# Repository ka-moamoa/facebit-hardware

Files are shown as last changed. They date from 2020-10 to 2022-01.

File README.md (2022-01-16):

# Smart PPE Hardware

The FaceBit circuit board contains all of the power harvesting, sense, and compute functionality demonstrated in the paper, plus a few extra capabilities we didn't use. This repository contains the Altium project with a [tagged release](https://github.com/ka-moamoa/facebit-hardware/releases/tag/paper-release) of the version manufactured for the paper. Note that Altium offers a [free student license](https://www.altium.com/solutions/academic-programs/student-licenses). 

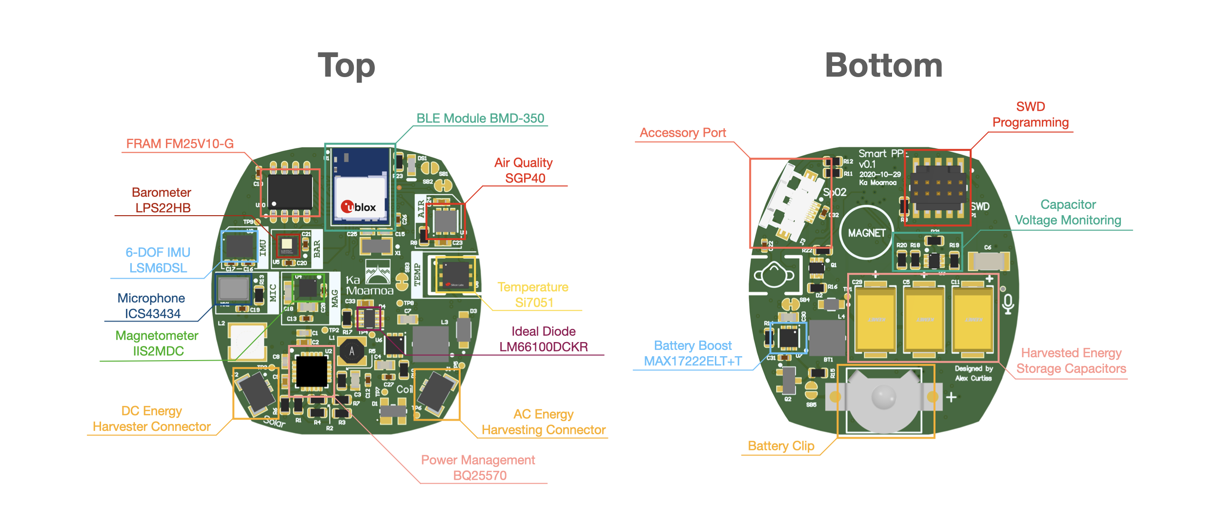
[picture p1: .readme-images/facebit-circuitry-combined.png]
Labeled Circuit Board


## Overview

FaceBit is small enough to fit comfortably in either an N95 or surgical mask (1.2" wide x 1.3" tall). It is clipped in place by 1) gluing a magnet to the underside of the board in the space provided, 2) positioning the board in the mask with the magnet facing toward the mask and 3) attaching a magnet to the other side. 

The board features an NRF2832 SoC from Nordic Semiconductor, which is packaged with a chip antenna on the pre-certified BMD-350 BLE Module. With a goal of using this platform to explore a wide range of health and environmental sensing applications, this version includes six sensors, which can be seen in the images. Only three are used in the paper: the LPS22HB barometer, the LSM6DSL 6-DOF Inertial Measurement Unit (IMU), and the Si7051 temperature sensor. In future versions, we expect to reduce the number of sensors and (therefore) reduce the size and cost of the board.

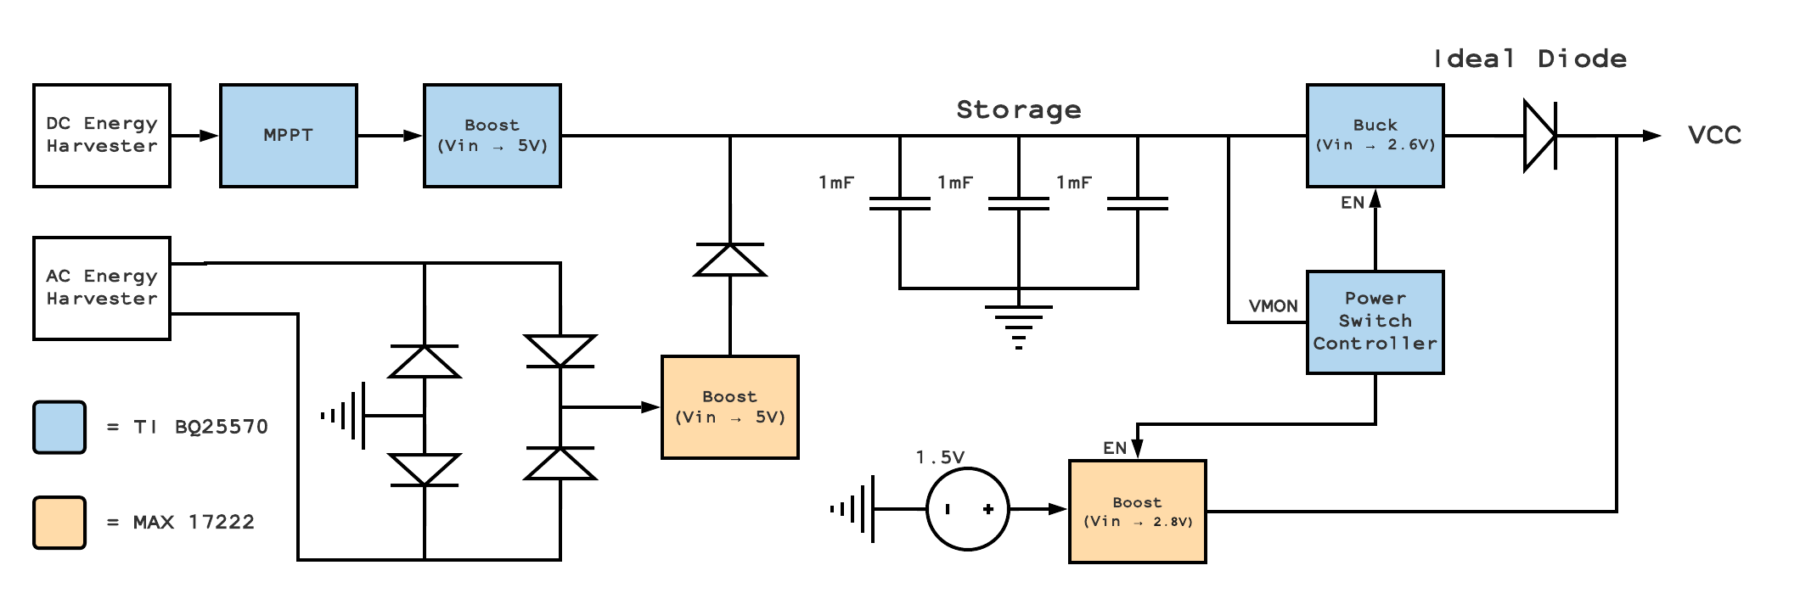
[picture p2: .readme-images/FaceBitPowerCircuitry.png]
Power Architecture
We adopt a flexible hybrid approach with regards to power:  We include a battery holder for a small, 105 mWh primary cell, but also include the circuitry and storage to power the board using energy harvested from both DC (e.g. solar) or AC (e.g. shaker) sources. Three tantalum capacitors on the bottom of the board combine to provide 3 mF of storage capacity for harvested energy. These are charged by Texas Instruments' BQ25570 power management IC, which incorporates a boost converter with MPPT, intelligent charging circuitry, and a buck converter to reduce the voltage from the storage elements to a level tolerated by the system. The tantalum capacitors are charged to 5V (80\% of their 6.3V rating), and so are able to store a total of 10.4 \(\mu\)Wh. We use the "power good" indicator on the BQ25570 IC to implement an intelligent switch that automatically decides which source to draw power from based on the voltage of the capacitors. By default, the system draws its power from the battery (when one is present). When the storage capacitor voltage exceeds a resistor-programmed threshold (3.0V in our application), the BQ25570 begins to draw from them and the battery boost converter is disabled, which protects the battery from reverse current.  When the storage capacitors fall below 2.6V, the BQ25570 switches off it's buck converter and system power is once again drawn from the battery. An ideal diode (LM66100DCKR) prevents reverse flow into the energy harvesting circuitry while the battery boost converter is active.

This power architecture allows for a relatively long battery life (the energy density of primary cells being greater than that of rechargeable cells), while still maintaining the ability to store and use harvested energy. The device can also operate in a mode where it uses only harvested energy, activated simply by not placing a battery in the connector. This flexible architecture suited the development process, but it is also possible to further simplify and miniaturize the board by using either only a rechargeable cell or only energy storage capacitors. 

### Errata

The tagged release includes fixes for the minor issues that required board rework after we received the boards (e.g. wrong resistor value). Still, some of the design choices, particularly those around the power architecture, limit the lowest possible sleep current of the board to around 30 uA. Version 2.0 is in the works which includes a revamped power architecture to address those issues.

The battery holder on this board is barely worth your time. It is ever so slightly too small for all of the batteries we were able to find, which means that over time it inevitably pops off the board, requiring a careful resoldering to the correct height. It's helpful to put a very thin layer of solder on the ground pad to facilitate contact with the battery.

Finally, as noted on the schematics the selected microphone unfortunately does not work with the NRF52. As you can see in [this issue](https://devzone.nordicsemi.com/f/nordic-q-a/24589/configuring-i2s-for-ics43434), the I2S frame width is incompatible with the nordic peripheral.

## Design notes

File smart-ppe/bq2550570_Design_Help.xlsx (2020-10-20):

User Input | VBIAS | 1.21 | V
Fixed
 | Comparator threshold for VSTOR of charger. |  |  |  |  | Comparator threshold voltages indicating when |  |  |  |  | For the bq25570 only, comparator threshold |  |  |  |  | Maximum power point threshold, e.g. ~0.7-0.8 of
 | Typically the max storage element voltage, |  |  |  |  | VSTOR has risen above VBAT_OK_HYST or fallen |  |  |  |  | for VOUT of buck converter. |  |  |  |  | solar panel's open circuit voltage.
 | e.g. 4.2V for LiIon battery. |  |  |  |  | below VBAT_OK.
 | VBAT_UV < VBAT_OV < 5.5V |  |  |  |  | VBAT_OV > VBAT_OK_HYST > VBAT_UV |  |  |  |  | 1.3V < VOUT < VBAT_OV |  |  |  |  | MPPT
Desired |  |  |  |  |  | RSUM1 | 13 | MW |  |  |  |  |  |  |  | RSUM1 | 20 | MW
Desired | RSUM1 | 13 | MW |  |  | VBAT_OK | 2.8 | V | > VBAT_UV |  | RSUM1 | 13 | MW |  |  | VIN_DC(OC) | 1 | V | Open Circuit Volts
Desired | VBAT_OV | 4 | V |  |  | VBAT_OK_HYST | 3.1 | V | > VBAT_OK |  | VOUT | 2.15 | V |  |  | VREF_SAMP | 0.9 | V | MPP voltage
 |  |  |  |  |  |  |  | closest 1% resistor1 |  |  |  |  |  |  |  |  |  | closest 1% resistor1
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

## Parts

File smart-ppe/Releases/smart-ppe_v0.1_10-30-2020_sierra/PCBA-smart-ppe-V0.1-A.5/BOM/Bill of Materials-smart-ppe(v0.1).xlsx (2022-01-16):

Line # | Name | Designator | Description | Manufacturer 1 | Manufacturer Part Number 1 | Manufacturer Lifecycle 1 | Supplier 1 | Supplier Part Number 1
 | 2988 | BT1 | BATTERY RETAINER COIN 7.9MM SMD | Keystone Electronics | 2988 | Volume Production | Newark | 25T0413
 | GRM155R60J475ME47D | C1 |  | Murata | GRM155R60J475ME47D | Volume Production | Digi-Key | 490-5915-6-ND
 | GRM155R71H103KA88D | C2 | Chip Capacitor, 10 nF, +/- 10%, 50 V, -55 to 125 degC, 0402 (1005 Metric), RoHS, Tape and Reel | Murata | GRM155R71H103KA88D | Volume Production | Arrow Electronics | GRM155R71H103KA88D
 | C1608X5R0J226M080AC | C3 | Chip Capacitor, 22 uF, +/- 20%, 6.3 V, -55 to 85 degC, 1608 (0603 Metric), RoHS, Tape and Reel | TDK | C1608X5R0J226M080AC | Volume Production | Newark | 65T7792
 | GRM188R60J106ME47D | C4 |  | Murata | GRM188R60J106ME47D | Volume Production | Arrow Electronics | GRM188R60J106ME47D
 | T495X108K006ATE100 | C5 | CAP TANT 1000UF 10% 6.3V 2917 | KEMET | T495X108K006ATE100 | Volume Production | Arrow Electronics | T495X108K006ATE100
 | C3216X5R1A107M160AC | C6 | Chip Capacitor, 100 uF, +/- 20%, 10 V, -55 to 85 degC, 1206 (3216 Metric), RoHS, Tape and Reel | TDK | C3216X5R1A107M160AC | Volume Production | Newark | 12T1945
 | GRM188R60J106ME47D | C7 |  | Murata | GRM188R60J106ME47D | Volume Production | Arrow Electronics | GRM188R60J106ME47D
 | GRM155R60J475ME47D | C8 |  | Murata | GRM155R60J475ME47D | Volume Production | Digi-Key | 490-5915-6-ND
 | GRM155R71H103KA88D | C9 | Chip Capacitor, 10 nF, +/- 10%, 50 V, -55 to 125 degC, 0402 (1005 Metric), RoHS, Tape and Reel | Murata | GRM155R71H103KA88D | Volume Production | Arrow Electronics | GRM155R71H103KA88D
 | Capacitor 100nF +/-20% 25V 0402 | C10 | Chip Capacitor, 100nF +/-20%, 25V, 0402, Thickness 0.6 mm | Samsung | CL05A104KA5NNNC | Volume Production | Newark | 82AC9174
 | T495X108K006ATE100 | C11 | CAP TANT 1000UF 10% 6.3V 2917 | KEMET | T495X108K006ATE100 | Volume Production | Arrow Electronics | T495X108K006ATE100
 | Capacitor 100nF +/-20% 25V 0402 | C12 | Chip Capacitor, 100nF +/-20%, 25V, 0402, Thickness 0.6 mm | Samsung | CL05A104KA5NNNC | Volume Production | Newark | 82AC9174
 | Capacitor 100nF +/-20% 25V 0402 | C13 | Chip Capacitor, 100nF +/-20%, 25V, 0402, Thickness 0.6 mm | Samsung | CL05A104KA5NNNC | Volume Production | Newark | 82AC9174
 | Capacitor 100nF +/-20% 25V 0402 | C14 | Chip Capacitor, 100nF +/-20%, 25V, 0402, Thickness 0.6 mm | Samsung | CL05A104KA5NNNC | Volume Production | Newark | 82AC9174
 | 04025A8R2JAT2A | C15 |  | Kyocera AVX | 04025A8R2JAT2A | Volume Production | Arrow Electronics | 04025A8R2JAT2A
 | Capacitor 100nF +/-20% 25V 0402 | C16 | Chip Capacitor, 100nF +/-20%, 25V, 0402, Thickness 0.6 mm | Samsung | CL05A104KA5NNNC | Volume Production | Newark | 82AC9174
 | Capacitor 100nF +/-20% 25V 0402 | C17 | Chip Capacitor, 100nF +/-20%, 25V, 0402, Thickness 0.6 mm | Samsung | CL05A104KA5NNNC | Volume Production | Newark | 82AC9174
 | CAP 220nF 25V 0603(1608) | C18 | CAP 220nF 25V ±10% 0603 (1608 Metric) Thickness 1mm SMD | Kyocera AVX | 06033C224KAT2A | Volume Production | Newark | 85R5672
 | Capacitor 100nF +/-20% 25V 0402 | C19 | Chip Capacitor, 100nF +/-20%, 25V, 0402, Thickness 0.6 mm | Samsung | CL05A104KA5NNNC | Volume Production | Newark | 82AC9174
 | Capacitor 100nF +/-20% 25V 0402 | C20 | Chip Capacitor, 100nF +/-20%, 25V, 0402, Thickness 0.6 mm | Samsung | CL05A104KA5NNNC | Volume Production | Newark | 82AC9174
 | Capacitor 100nF +/-20% 25V 0402 | C21 | Chip Capacitor, 100nF +/-20%, 25V, 0402, Thickness 0.6 mm | Samsung | CL05A104KA5NNNC | Volume Production | Newark | 82AC9174
 | Capacitor 100nF +/-20% 25V 0402 | C22 | Chip Capacitor, 100nF +/-20%, 25V, 0402, Thickness 0.6 mm | Samsung | CL05A104KA5NNNC | Volume Production | Newark | 82AC9174
 | CC0402KRX5R5BB105 | C23 | Chip Capacitor, 1 uF, +/- 10%, 6.3 V, -55 to 85 degC, 1005 (0402 Metric), RoHS, Tape and Reel | Yageo | CC0402KRX5R5BB105 | Volume Production | Newark | 65R7644
 | CC0402KRX5R5BB105 | C24 | Chip Capacitor, 1 uF, +/- 10%, 6.3 V, -55 to 85 degC, 1005 (0402 Metric), RoHS, Tape and Reel | Yageo | CC0402KRX5R5BB105 | Volume Production | Newark | 65R7644
 | 04025A8R2JAT2A | C25 |  | Kyocera AVX | 04025A8R2JAT2A | Volume Production | Arrow Electronics | 04025A8R2JAT2A
 | Capacitor 100nF +/-20% 25V 0402 | C26 | Chip Capacitor, 100nF +/-20%, 25V, 0402, Thickness 0.6 mm | Samsung | CL05A104KA5NNNC | Volume Production | Newark | 82AC9174
 | Capacitor 100nF +/-20% 25V 0402 | C27 | Chip Capacitor, 100nF +/-20%, 25V, 0402, Thickness 0.6 mm | Samsung | CL05A104KA5NNNC | Volume Production | Newark | 82AC9174
 | GRM188R60J106ME47D | C28 |  | Murata | GRM188R60J106ME47D | Volume Production | Arrow Electronics | GRM188R60J106ME47D
 | T495X108K006ATE100 | C29 | CAP TANT 1000UF 10% 6.3V 2917 | KEMET | T495X108K006ATE100 | Volume Production | Arrow Electronics | T495X108K006ATE100
 | GRM188R60J106ME47D | C30 |  | Murata | GRM188R60J106ME47D | Volume Production | Arrow Electronics | GRM188R60J106ME47D
 | Capacitor 100nF +/-20% 25V 0402 | C31 | Chip Capacitor, 100nF +/-20%, 25V, 0402, Thickness 0.6 mm | Samsung | CL05A104KA5NNNC | Volume Production | Newark | 82AC9174
 | Capacitor 100nF +/-20% 25V 0402 | C32 | Chip Capacitor, 100nF +/-20%, 25V, 0402, Thickness 0.6 mm | Samsung | CL05A104KA5NNNC | Volume Production | Newark | 82AC9174
 | CC0402KRX5R5BB105 | C33 | Chip Capacitor, 1 uF, +/- 10%, 6.3 V, -55 to 85 degC, 1005 (0402 Metric), RoHS, Tape and Reel | Yageo | CC0402KRX5R5BB105 | Volume Production | Newark | 65R7644
 | BAS3007A-RPP | D1 | Low VF Schottky Diode Array, 30 V VR, 900 mA IF, SOT143, Reel, Green | Infineon | BAS3007A-RPP | Volume Production | Arrow Electronics | BAS3007ARPPE6327HTSA1
 | BAT54HT1G | D2 | Schottky Barrier Diode, 2-Pin SOD-323, Pb-Free, Tape and Reel | ON Semiconductor / Fairchild | BAT54HT1G | Volume Production | Future Electronics | 7645070
 | BZT52C5V1-7-F | D3 | Surface Mount Zener Diode, 5.1 V, -65 to 150 degC, 2-Pin SMD (SOD-123), RoHS, Tape and Reel | Diodes | BZT52C5V1-7-F | Volume Production | Newark | 81AC7614
 | LM66100DCKR | D4 | Diode | Texas Instruments | LM66100DCKR | Unknown | Digi-Key | 296-53541-1-ND
 | HSMG-C190 | DS1 | Chip LED, Green, 2.2 V, -40 to 85 degC, 2-Pin SMD, RoHS, Tape and Reel | Broadcom Avago | HSMG-C190 | Volume Production | Mouser | 630-HSMG-C190
 | SM02B-SURS-TF_LF__SN | J1 | Connector | JST (JAPAN SOLDERLESS TERMINALS) | SM02B-SURS-TF(LF)(SN)
 | SM02B-SURS-TF(LF)(SN) | J2 | Connector | JST (JAPAN SOLDERLESS TERMINALS) | SM02B-SURS-TF(LF)(SN)
 | 54550-0571 | J3 | 0.5 mm Pitch Easy-On(TM) Type FPC Connector, 1.2 mm Mated Height, Right Angle, ZIF, SMT, Top Contact, 5 Circuits, -20 to 85 degC, ELV and RoHS Compliant, Tape and Reel | Molex | 54550-0571 | Volume Production | Digi-Key | WM8824DKR-ND
 | 744029100 | L1 | SMD Shielded Tiny Power Inductor WE-TPC, L = 10.0 µH | Wurth Electronics | 744029100 | Volume Production | Digi-Key | 732-1091-1-ND
 | 744031220 | L2 | SMD Shielded Tiny Power Inductor WE-TPC, L = 22.0 µH | Wurth Electronics | 744031220 | Volume Production | Digi-Key | 732-1012-6-ND
 | 74438357022 | L3 | WURTH ELEKTRONIK - 74438357022 - INDUCTOR, 2.2UH, 5.2A, 20%, SHIELDED | Wurth Electronics | 74438357022 | Unknown | Digi-Key | 732-11201-6-ND
 | 74438357022 | L4 | WURTH ELEKTRONIK - 74438357022 - INDUCTOR, 2.2UH, 5.2A, 20%, SHIELDED | Wurth Electronics | 74438357022 | Unknown | Digi-Key | 732-11201-6-ND
 | Mic_InvenSense_ICS-43434_eec | MK1 | MIC MEMS MULTI-MODE OMNI -26DB | TDK InvenSense | ICS-43434 | New Product | Digi-Key | 1428-1066-6-ND
 | FTSH-105-01-F-DV-K-P-TR | P1 | CONN HEADER SMD 10POS 1.27MM | Samtec | FTSH-105-01-F-DV-K-P-TR | Volume Production | Newark | 25AC9619
 | DMC2400UV-7 | Q1 | Complementary Pair Enhancement Mode MOSFET, 20 V N-Channel, -20 V P-Channel, -55 to 150 degC, 6-Pin SOTFL (SOT563), RoHS, Tape and Reel | Diodes | DMC2400UV-7 | Volume Production | Newark | 79AH1251
 | SI2323DS-T1-E3 | Q2 | P-Channel MOSFET, 20 V, -55 to 150 degC, 3-Pin TO-236, RoHS, Tape and Reel | Vishay | SI2323DS-T1-E3 | Volume Production | Newark | 06J7584
 | DMC2400UV-7 | Q3 | Complementary Pair Enhancement Mode MOSFET, 20 V N-Channel, -20 V P-Channel, -55 to 150 degC, 6-Pin SOTFL (SOT563), RoHS, Tape and Reel | Diodes | DMC2400UV-7 | Volume Production | Newark | 79AH1251
 | RES_0603 | R1 | Resistor Ω % 0603 | Vishay | CRCW06038M25FKEA |  | Digi-Key | 541-8.25MHCT-ND
 | RES_0603 | R2 | Resistor Ω % 0603 | Vishay | CRCW06033M01FKEA |  | Digi-Key | 541-3.01MHCT-ND
 | RES_0603 | R3 | Resistor Ω % 0603 | Vishay | CRCW06037M15FKEA |  | Digi-Key | 541-7.15MHCT-ND
 | RES_0603 | R4 | Resistor Ω % 0603 | Stackpole Electronics | RMCF0603FT4M64 |  | Digi-Key | RMCF0603FT4M64CT-ND
 | RES_0603 | R5 | Resistor Ω % 0603 | Vishay | CRCW06035M62FKEA |  | Digi-Key | 541-5.62MHCT-ND
 | RES_0603 | R6 | Resistor Ω % 0603 | Stackpole Electronics | RMCF0603FT4M64 |  | Digi-Key | RMCF0603FT4M64CT-ND
 | RES_0603 | R7 | Resistor Ω % 0603 | Vishay | CRCW06035M23FKEA |  | Digi-Key | 541-5.23MHCT-ND
 | RES_0603 | R8 | Resistor Ω % 0603 | Yageo | RC0603FR-074R7L |  | Digi-Key | YAG3371CT-ND
 | RES_0603 | R9 | Resistor Ω % 0603 | Panasonic | ERJ-3EKF4701V |  | Digi-Key | P4.70KHCT-ND
 | RES_0603 | R10 | Resistor Ω % 0603 | Stackpole Electronics | HMC0603JT33M0 |  | Digi-Key | HMC0603JT33M0CT-ND
 | RES_0603 | R11 | Resistor Ω % 0603 | Panasonic | ERJ-3EKF4701V |  | Digi-Key | P4.70KHCT-ND
 | RES_0603 | R12 | Resistor Ω % 0603 | Panasonic | ERJ-3EKF4701V |  | Digi-Key | P4.70KHCT-ND
 | RES_0603 | R13 | Resistor Ω % 0603 | Yageo | RC0603FR-07100KL |  | Digi-Key | 311-100KHRCT-ND
 | RES_0603 | R14 | Resistor Ω % 0603 | Vishay | CRCW0603536RFKEA |  | Digi-Key | 541-536HCT-ND
 | RES_0603 | R15 | Resistor Ω % 0603 | Samsung | RC1608F335CS |  | Arrow Electronics | RC1608F335CS
 | RES_0603 | R16 | Resistor Ω % 0603 | Vishay | CRCW06031M00FKEA |  | Digi-Key | 541-1.00MHCT-ND
 | RES_0603 | R17 | Resistor Ω % 0603 | Vishay | CRCW06031M00FKEA |  | Digi-Key | 541-1.00MHCT-ND
 | RES_0603 | R18 | Resistor Ω % 0603 | Vishay | CRCW0603180KFKEA |  | Digi-Key | 541-180KHCT-ND
 | RES_0603 | R19 | Resistor Ω % 0603 |  |  |  | Digi-Key | 541-1.00MHCT-ND
 | RES_0603 | R20 | Resistor Ω % 0603 | Yageo | RC0603FR-07100KL |  | Digi-Key | 311-100KHRCT-ND
 | RES_0603 | R21 | Resistor Ω % 0603 | Vishay | CRCW06031M00FKEA |  | Digi-Key | 541-1.00MHCT-ND
 | RES_0603 | R22 | Resistor Ω % 0603 | Vishay | CRCW06031M00FKEA |  | Digi-Key | 541-1.00MHCT-ND
 | RES_0603 | R23 | Resistor Ω % 0603 | Panasonic | ERJ3EKF4700V |  | Digi-Key | P470HCT-ND
 | BMD-350 | U1 | u-blox BMD-350 Bluetooth 5 module | u-blox | BMD-350-A-R | Unknown | Digi-Key | 672-BMD-350-A-RDKR-ND
 | BQ25570RGRR | U2 | Battery Management Low Pwr Harvester Pwr Mgmt IC | Texas Instruments | BQ25570RGRR | Volume Production | Arrow Electronics | BQ25570RGRR
 | LSM6DSLTR | U3 | iNEMO Inertial Module:Always-on 3D Accelerometer and 3D Gyroscope, 1.71 to 3.6 V, -40 to 85 degC, 14-Pin LGA, RoHS, Tape and Reel | STMicroelectronics | LSM6DSLTR | Not Recommended for New Design | Arrow Electronics | LSM6DSLTR
 | IIS2MDCTR | U4 | HIGH ACCURACY ULTRA-LOW-POWER 3- | STMicroelectronics | IIS2MDCTR | Unknown | Digi-Key | 497-17728-6-ND
 | LPS22HBTR | U5 | MEMS NANO PRESSURE SENSOR: 260-1 | STMicroelectronics | LPS22HBTR | Volume Production | Arrow Electronics | LPS22HBTR
 | MAX17222ELT+T | U6 | IC REG BOOST ADJ .5A NANO 6UDFN | Maxim | MAX17222ELT+T | Unknown | Mouser | 700-MAX17222ELT+T
 | MAX17222ELT+T | U7 | IC REG BOOST ADJ .5A NANO 6UDFN | Maxim | MAX17222ELT+T | Unknown | Mouser | 700-MAX17222ELT+T
 | SI7051-A20-IM | U8 | SENSOR DIGITAL -40C-125C 6DFN | Silicon Labs | SI7051-A20-IM | Volume Production | Arrow Electronics | SI7051-A20-IM
 | SGP40-D-R4 | U9 | SGP40 Series 3.6 V 4 mA Indoor Air Quality Sensor for VOC Measurements - DFN-6 | Sensirion | SGP40-D-R4 | Unknown | Arrow Electronics | SGP40-D-R4
 | FM25V10-G | U10 | 1-Mbit Serial F-RAM, 2 to 3.6 V, -40 to 85 degC, 8-Pin SOIC (S08.15), RoHS, Tube | Cypress | FM25V10-G | Not Recommended for New Design | Future Electronics | 1995372
 | ABS07-32.768KHz-T | X1 | Crystal, 32.768 kHz, 12.5 pF, -40 to 85 degC, SMD Low Profile 3.2 x 1.5 x 0.9 mm, Tape and Reel | Abracon | ABS07-32.768KHZ-T | Volume Production | Newark | 14N8749

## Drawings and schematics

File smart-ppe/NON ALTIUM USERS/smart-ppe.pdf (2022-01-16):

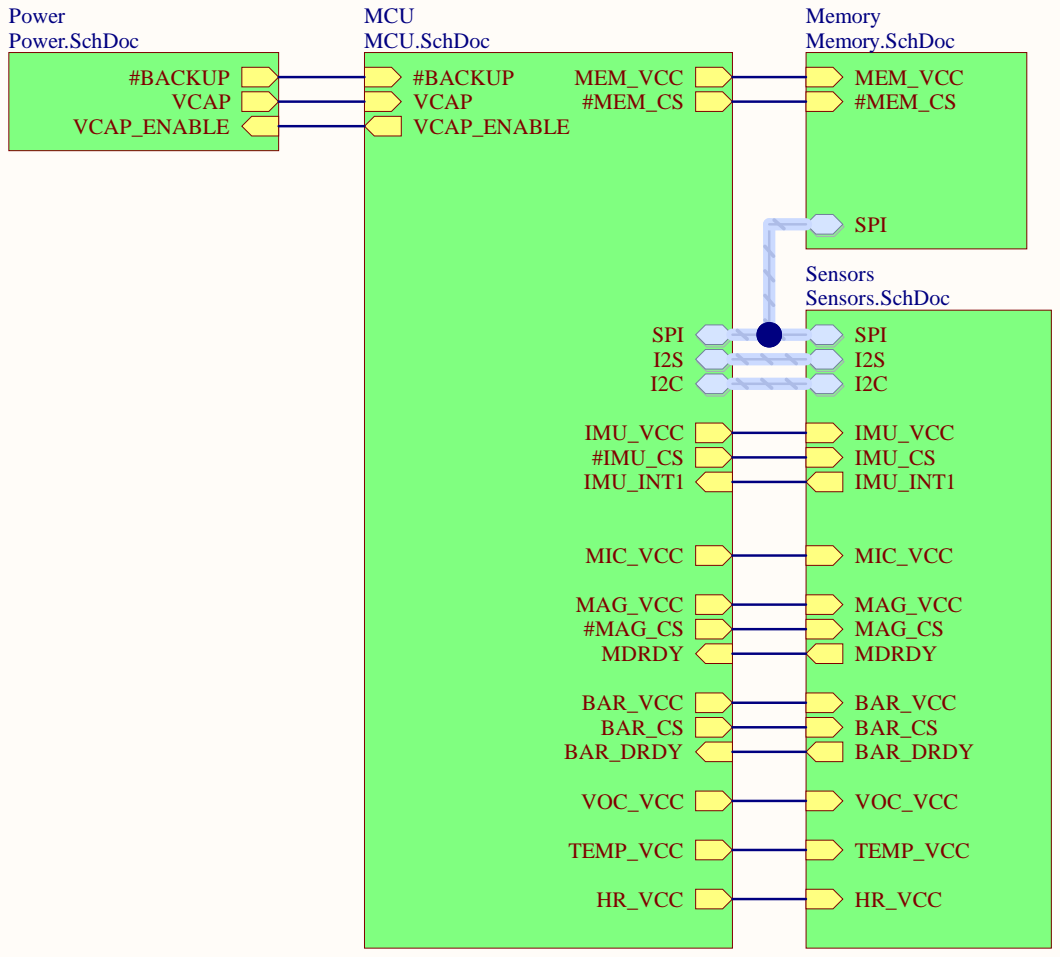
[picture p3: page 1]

E-Mail: alexander.curtiss@u.northwestern.edu

Ka Moamoa
Northwestern University
http://kamoamoa.eecs.northwestern.edu/

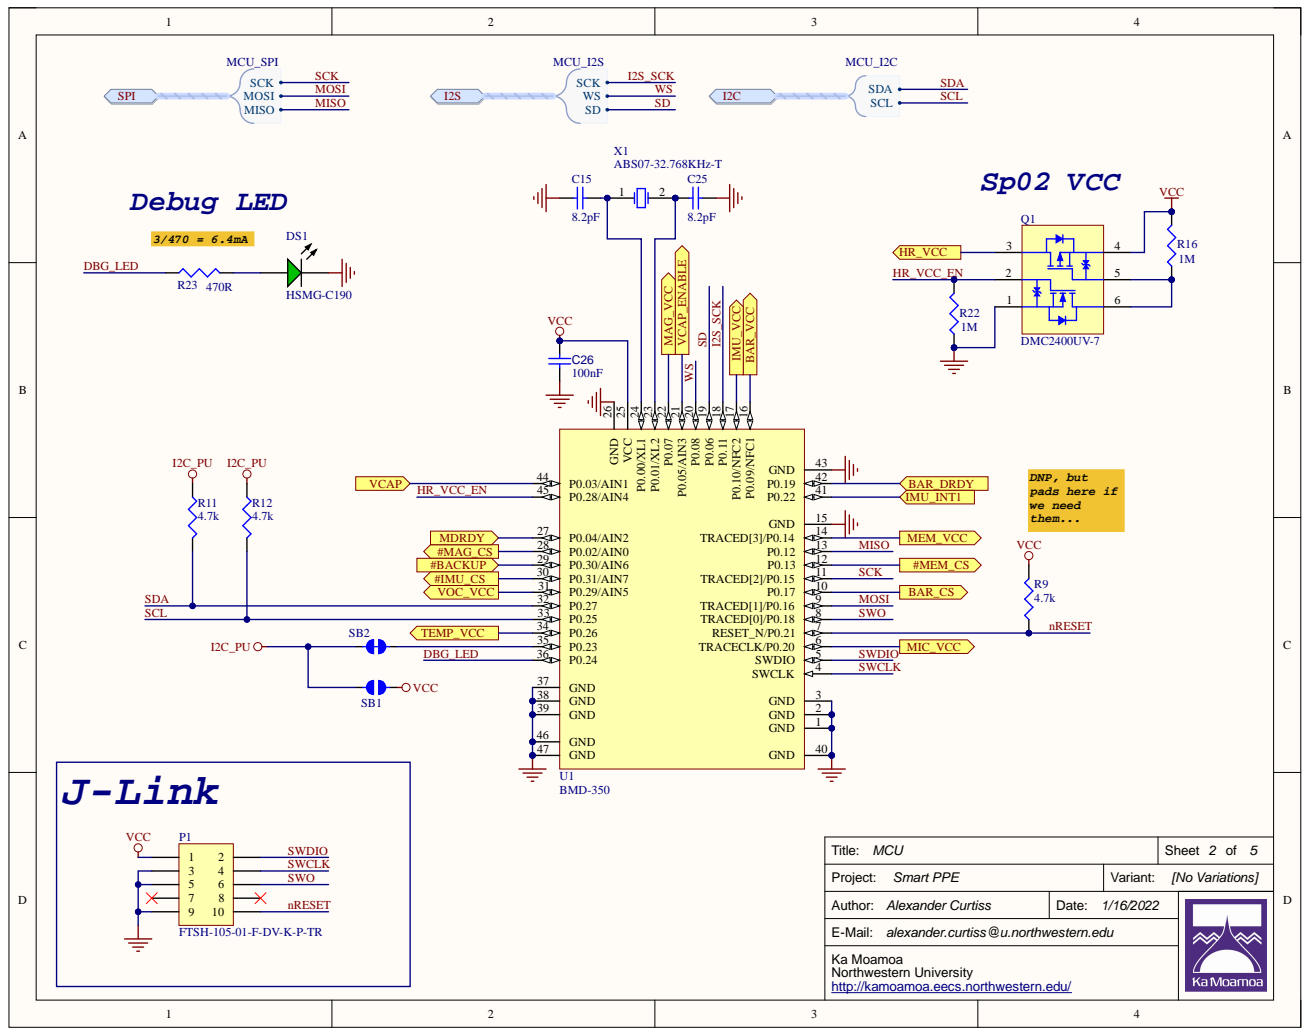
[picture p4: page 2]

E-Mail: alexander.curtiss@u.northwestern.edu

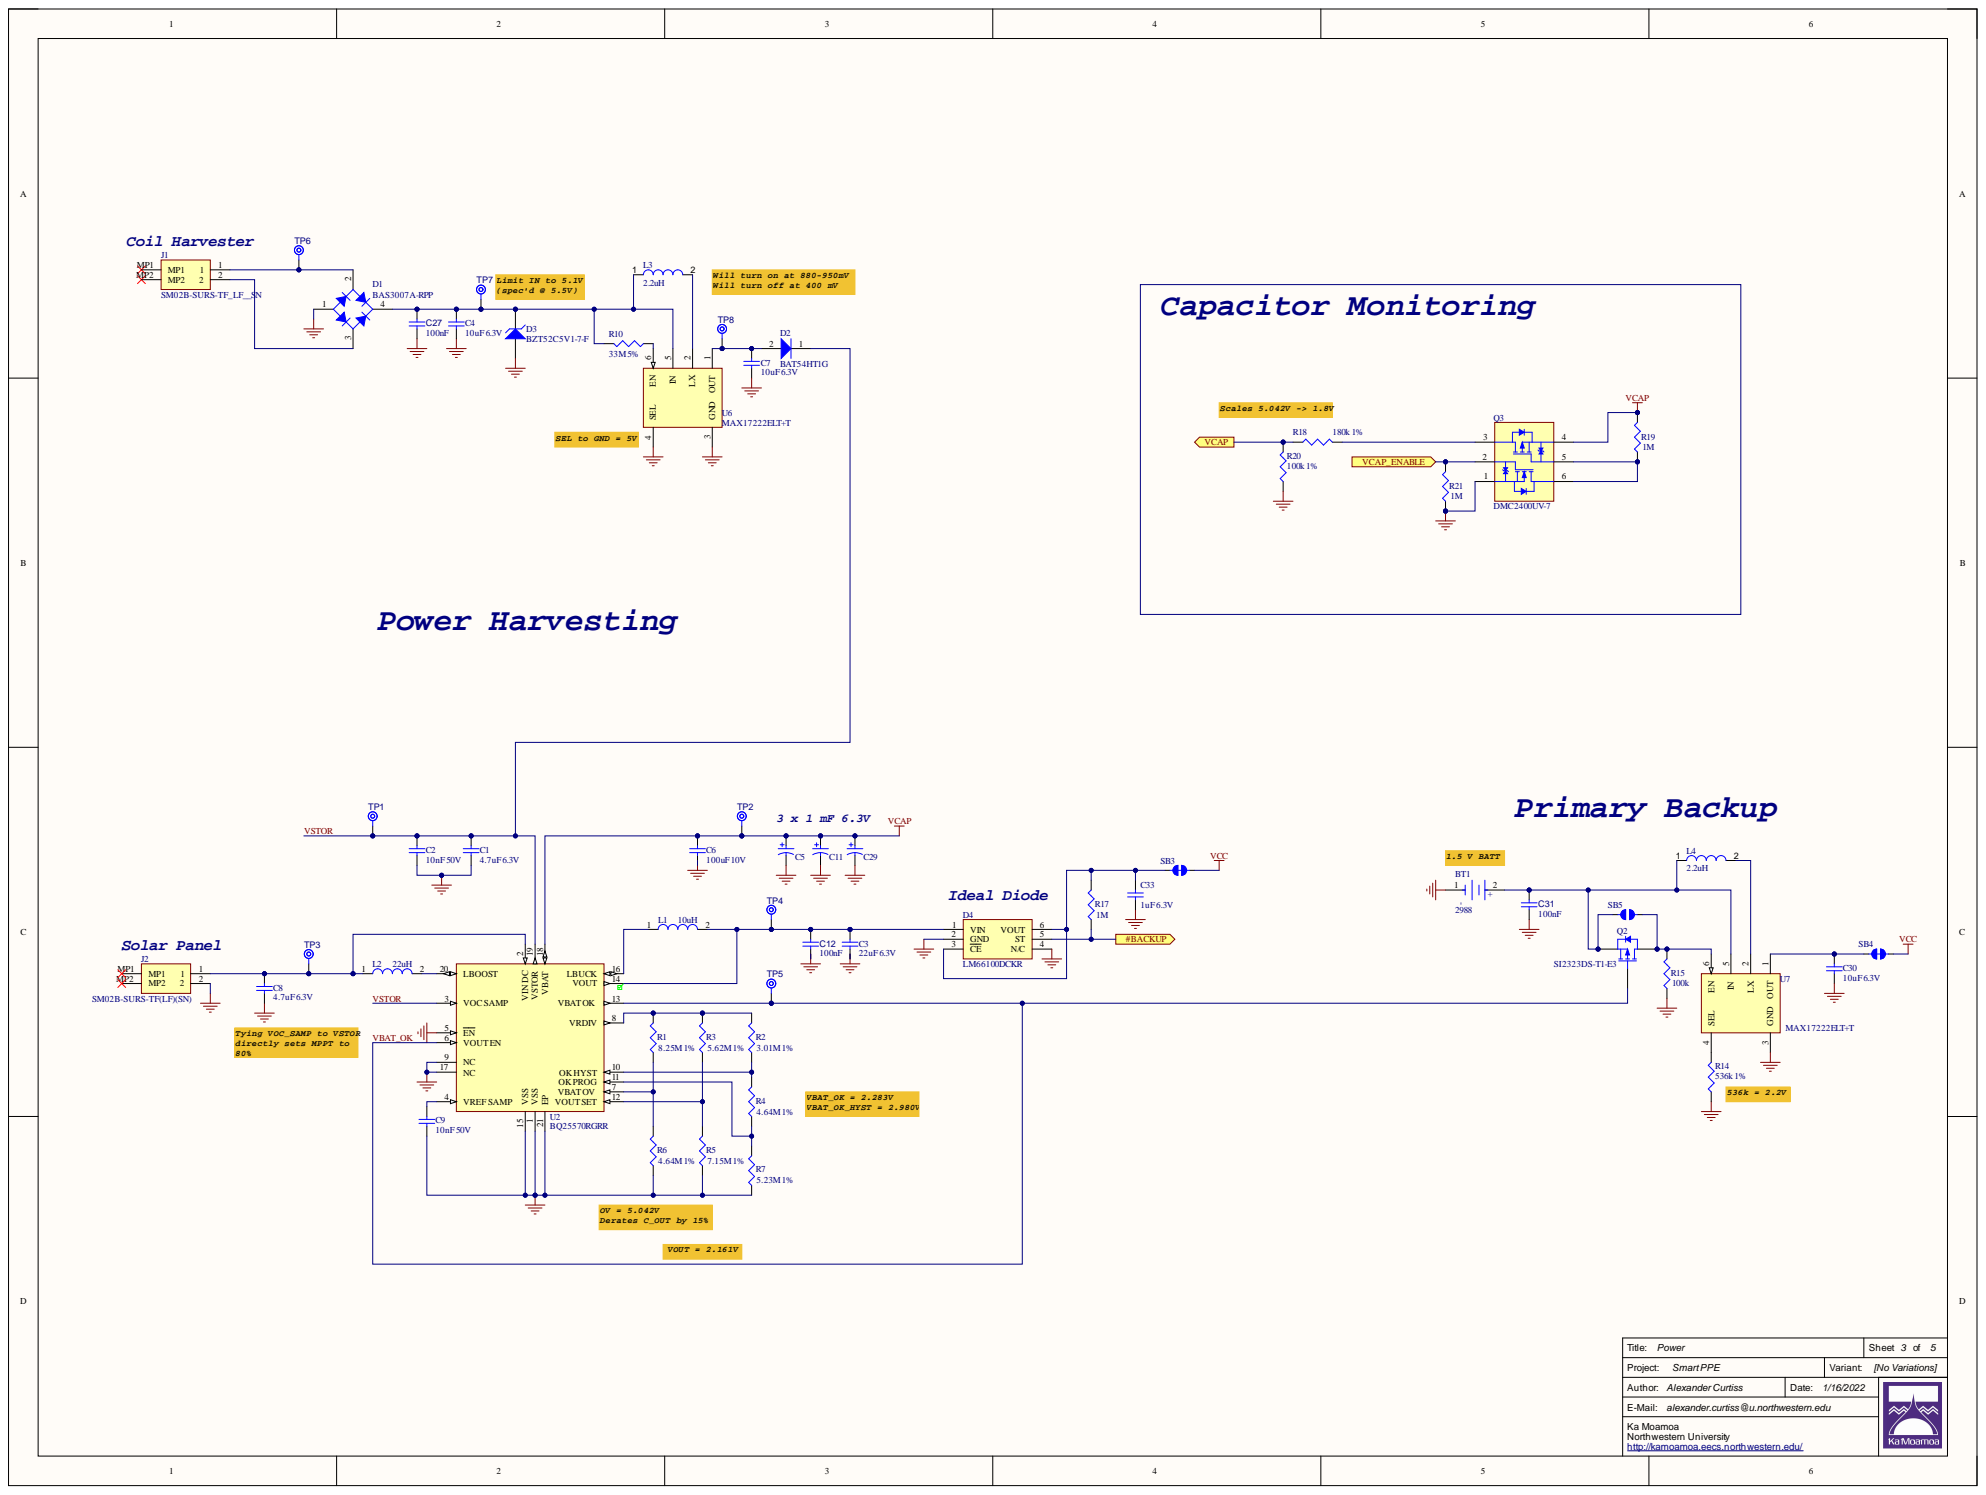
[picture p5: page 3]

Will turn on at 880-950mV
Will turn off at 400 mV

SM02B-SURS-TF(LF)(SN)

Tying VOC_SAMP to VSTOR
directly sets MPPT to

E-Mail: alexander.curtiss@u.northwestern.edu

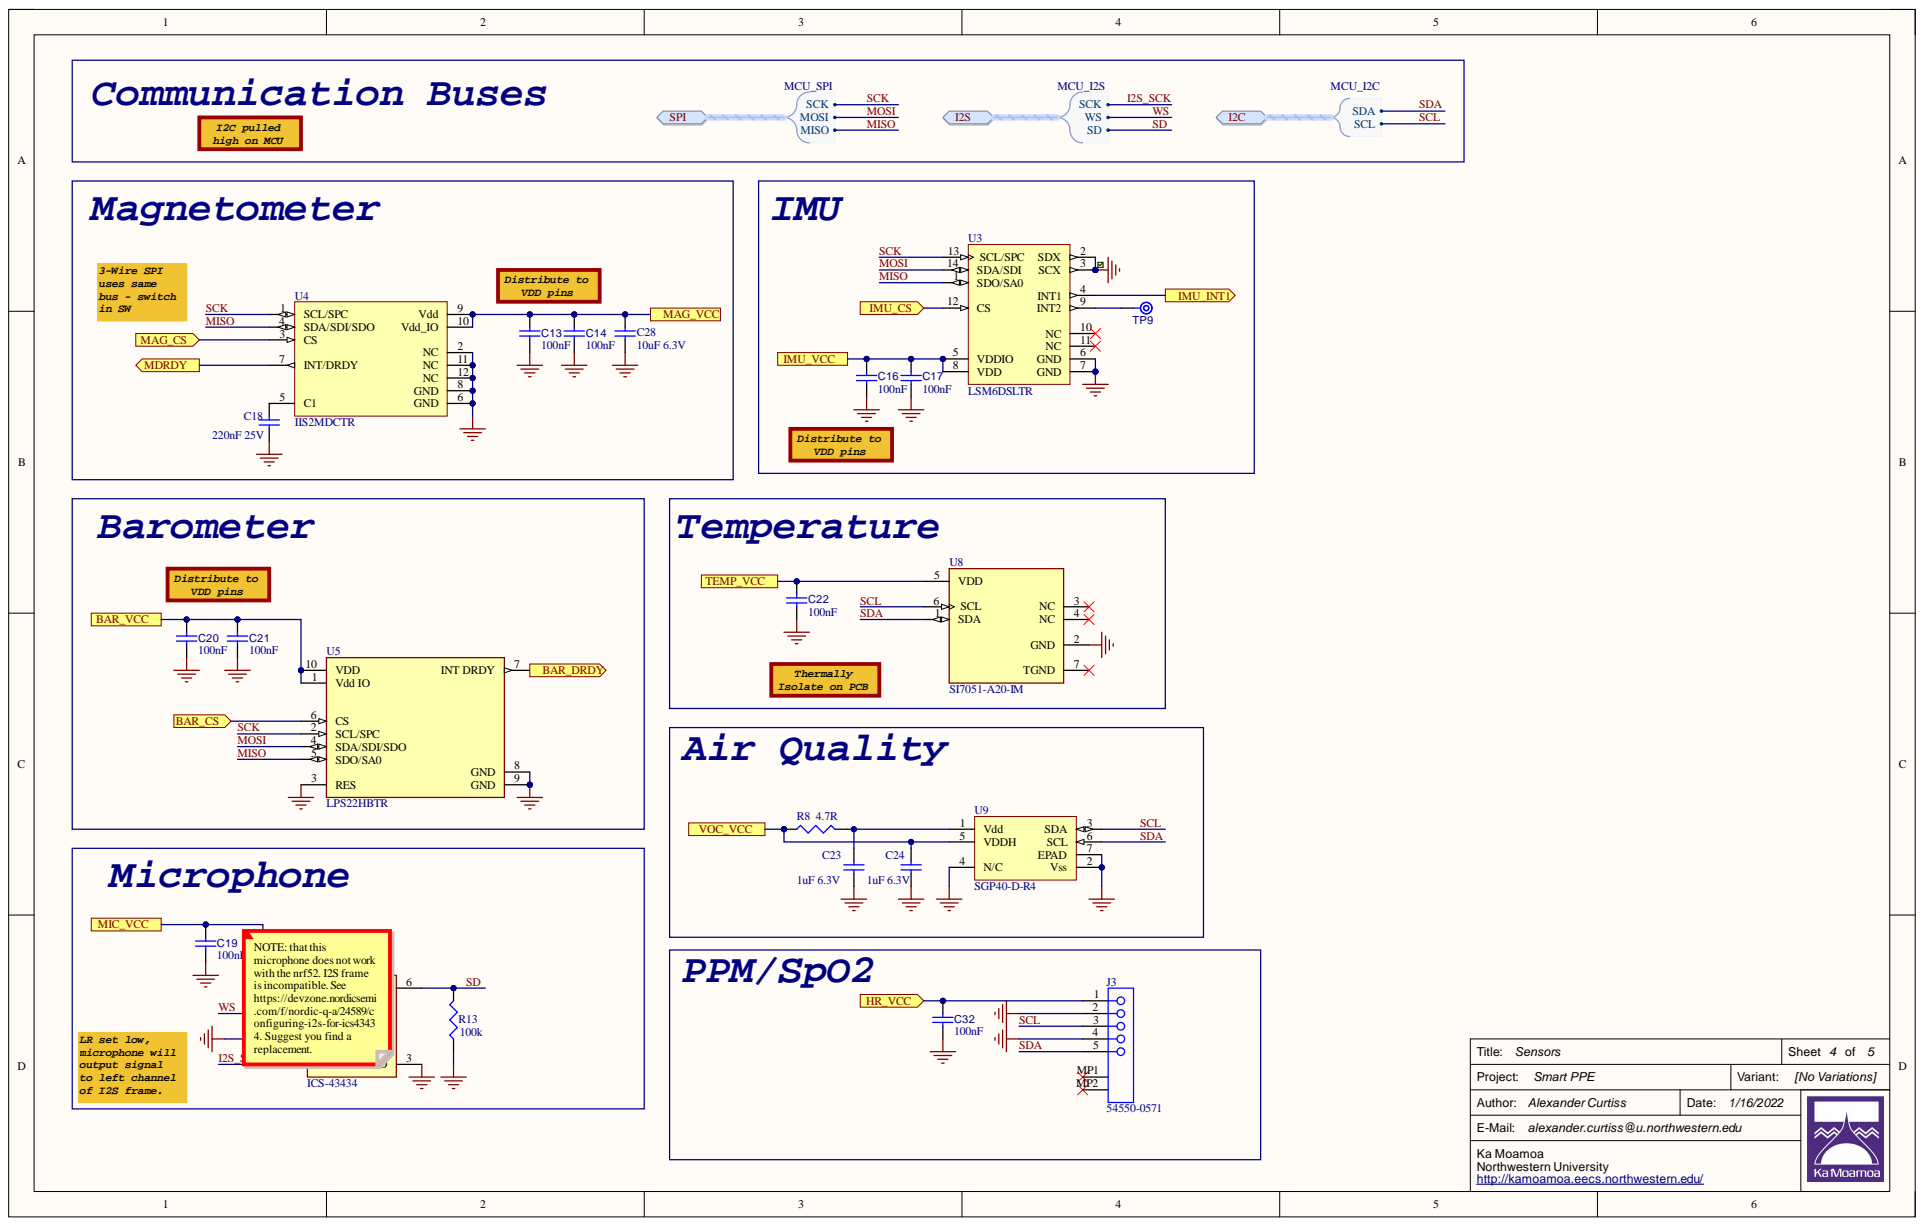
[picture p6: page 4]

MIC_VCC | C19

NOTE: that this
microphone does not work
with the nrf52. I2S frame
isincompatible. See
https://devzone.nordicsemi
.com/f/nordic-q-a/24589/c
onfiguring-i2s-for-ics4343
4. Suggest you find a
replacement.

Project: Smart PPE | Variant: [No Variations]

Author: Alexander Curtiss | Date: 1/16/2022

E-Mail: alexander.curtiss@u.northwestern.edu

Ka Moamoa
Northwestern University
http://kamoamoa.eecs.northwestern.edu/

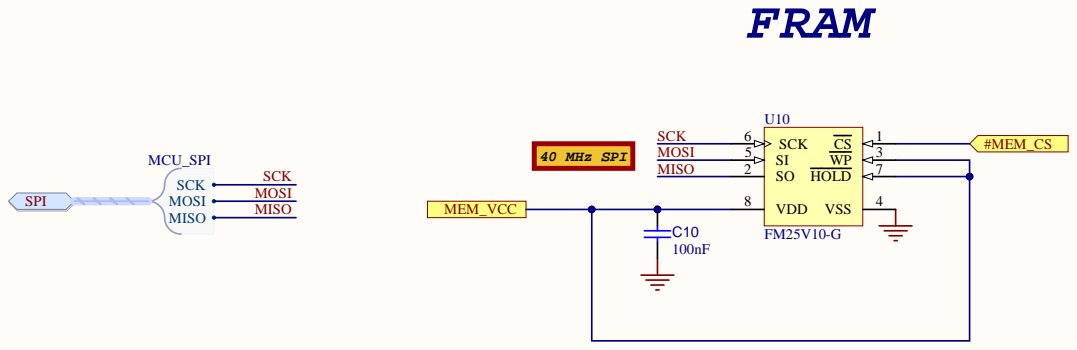
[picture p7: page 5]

40 MHz SPI | I 5

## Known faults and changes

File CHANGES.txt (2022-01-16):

Anyone modifying the design should provide brief information about the modifications, including the date they were made, in this file.

Information about the design should be added to but never removed from this file.

According to section 3.3b of the CERN OHL license, licensees should provide a brief entry with a date and the nature of the modification for each design change. 

For example:

2022-01-16 - Alexander Curtiss apcurtiss@gmail.com

Added note to schematic regarding microphone incompatability with MCU.

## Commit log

2020-09-18 add top level schematic doc and blank pcb doc
    [Top.SchDoc, smart-ppe.PcbDoc, smart-ppe.PrjPcb]
2020-09-18 Update with ka moamoa schematic template
    [Top.SchDoc, smart-ppe.PrjPcb]
2020-10-10 schematic first draft
    [MCU.SchDoc, Memory.SchDoc, Power.SchDoc, Sensors.SchDoc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]
2020-10-10 add schematic pdf print
2020-10-15 resolve compilation errors, adjust vout to ~2.15V, assign passive components
    [MCU.SchDoc, Memory.SchDoc, Power.SchDoc, Sensors.SchDoc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]
2020-10-20 saving state before re-arranging to accommodate battery
2020-10-20 actually saving state before re-arranging to accommodate battery
    [MCU.SchDoc, Power.SchDoc, Sensors.SchDoc, bq2550570_Design_Help.xlsx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]
2020-10-22 major schematic edits
    - swap supercap with tantalums
    - add primary cell battery backup as failsafe (w/supporting circuitry)
    - add capacitor voltage monitoring
    - improve spo2 sensor voltage supply
    - add configurable i2c pull-up rail
    [MCU.SchDoc, Memory.SchDoc, Power.SchDoc, Sensors.SchDoc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]
2020-10-27 pcb progress. routing almost complete.
    [MCU.SchDoc, Memory.SchDoc, Power.SchDoc, Top.SchDoc]
2020-10-28 routing complete. no DRC errors
    [Power.SchDoc]
2020-10-28 pushing unsaved changes
    [smart-ppe.PrjPcb]
2020-10-28 Add pours to VCC
    [smart-ppe.PrjPcb]
2020-10-29 Post-review edits complete. Added logo and version text.
    [Power.SchDoc, Sensors.SchDoc]
2020-10-29 Add outjobs
    [MCU.SchDoc, Power.SchDoc, Sensors.SchDoc, smart-ppe.PrjPcb]
2020-10-29 Mdofy assembly outjob
    [MCU.SchDoc, Memory.SchDoc, Power.SchDoc, Sensors.SchDoc]
2020-10-29 increment to v0.1
    [smart-ppe.PrjPcb]
2020-10-29 add board outline layer to gerbers x_x
2020-10-29 Simplify release package, add board information to gerbers
2020-11-01 swap vcap pin
    [MCU.SchDoc]
2020-12-17 update power
    - resistor swap
    - primary boost resistor
    - FET resistor
    [Power.SchDoc]
2022-01-16 roll back to project release hw. add pdf and 3d files for those without altium. add CERN OHL-S information
    [Bill of Materials-smart-ppe(v0.1).xlsx, Sensors.SchDoc, smart-ppe.GBL, smart-ppe.GBO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]
